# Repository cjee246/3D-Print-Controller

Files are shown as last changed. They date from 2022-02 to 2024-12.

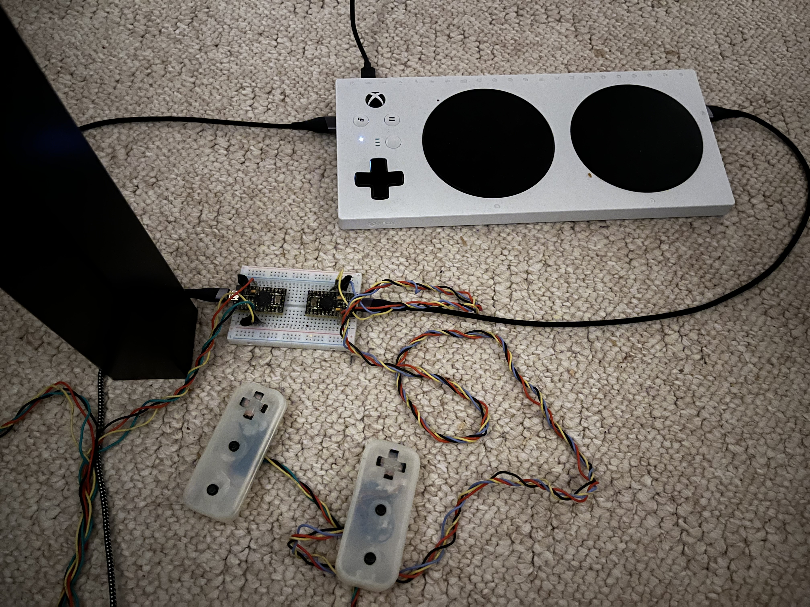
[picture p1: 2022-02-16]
Physical/3D-print control setup.jpg

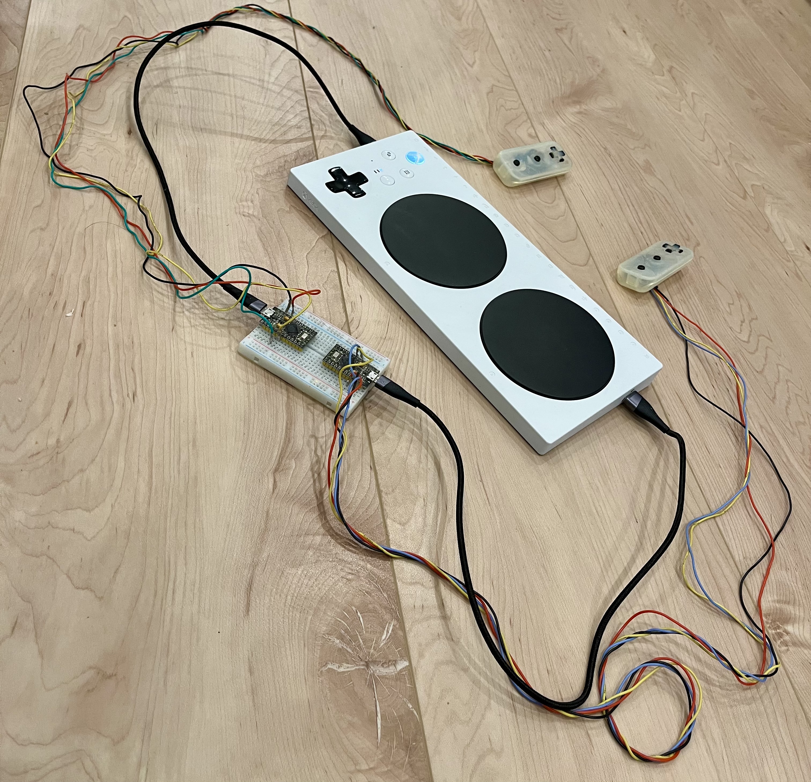
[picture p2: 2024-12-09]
Physical/Controller Assembly.jpg

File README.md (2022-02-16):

# 3D-Print-Controller
Custom made 3D-printed zero-force touch sensitive controller to accommodate chronic pain disability

- see ../0_Single Control for code using configurable controller orientation
- see ../1_Dual Control for code using two controller configuration
- see ../Physical for step files and physical image used in conjunction with xbox adaptive controller

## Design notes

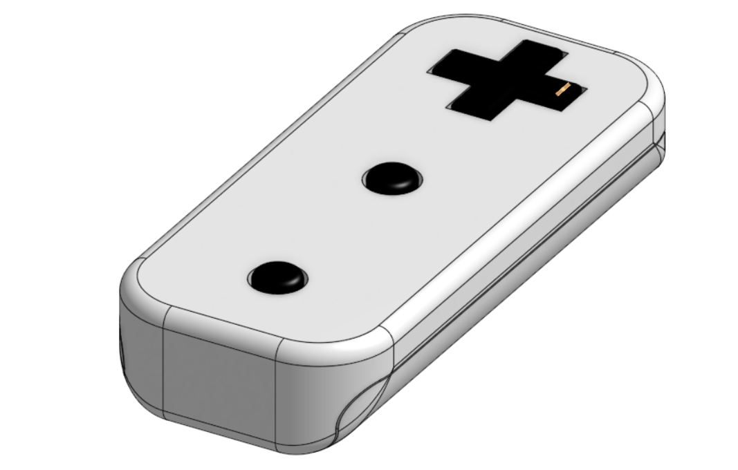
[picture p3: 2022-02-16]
Physical/ctrl.png

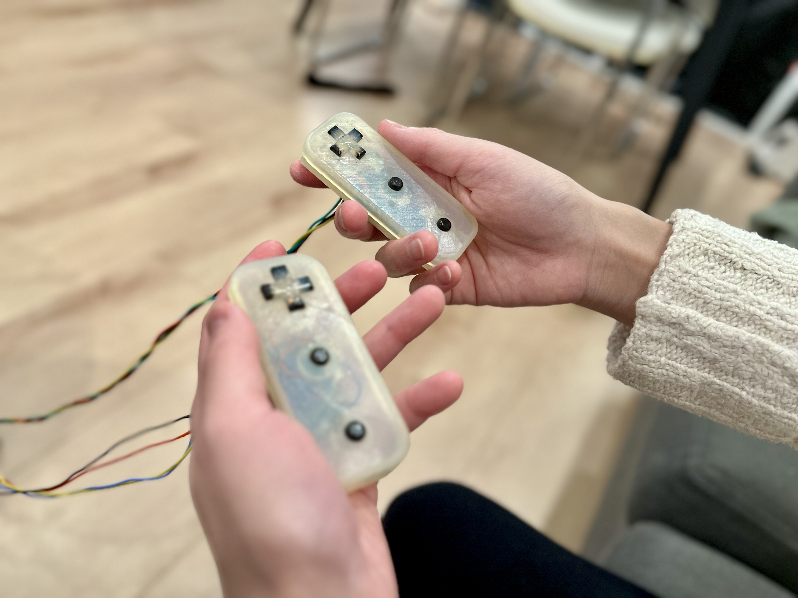
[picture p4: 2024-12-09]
Physical/Controller Held.jpg

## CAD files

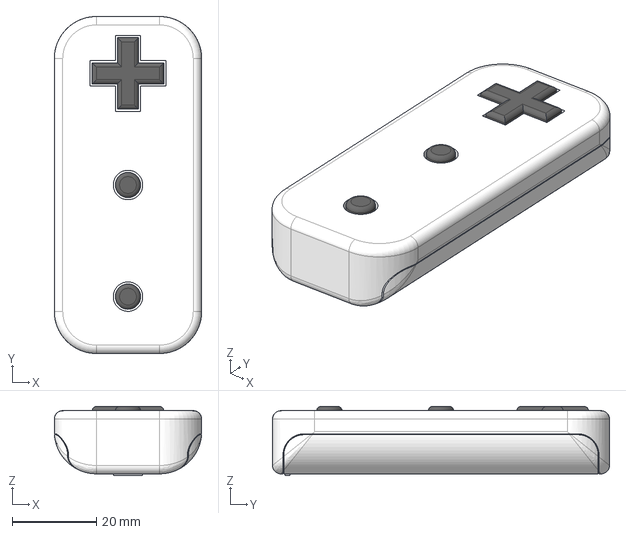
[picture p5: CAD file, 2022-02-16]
Physical/Controller.step
35.0 x 80.0 x 16.4 mm

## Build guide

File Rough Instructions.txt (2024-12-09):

Rough Instructions:
- Sorry for the lack of images, I'm doing this very after the fact

***

Materials:
- 3D printer access
- copper foil tape
- conductive paint
	- I used Bare Conductive Paint
	- This can be excluded if you wish to use copper foil, but it looks sleeker with the paint
- clear spray paint
	- I used Rust-Oleum Painter's Touch 2X Ultra Cover Multi-Purpose Paint And Primer in Semi-Gloss Clear
- wiring
	- I used 28 AWG cut to length and manually crimped coming out of the controller - this means one needs crimps and a crimping tool
		- Alternatively, you can use pre-crimped jumper cables for testing
	- I used 30 AWG wiring for the internals
- soldering equipment
	- Soldering iron, solder, flux, fume extraction, alligator clips, etc.
- Hot glue
	- For fixing the internal wiring in place
- breadboard
- Arduino Pro Micro Atmega32U4 
	- 2 of these if you're doing dual control support
- Capacitive Touch Sensors
	- I used Adafruit 12-Key Capacitive Touch Sensor Breakout - MPR121
- USB-A to micro-USB cable
	- 2 of these if you're doing dual control support

***

Flash code to Arduino Micro Controller
- Micro USB to USB-A into your computer
- If using dual control mode, note that there is a Left and Right Ctrl to flash for each one

Print 3D Model
- 5 pieces
	- 2 buttons
	- 1 d-pad
	- 1 body
	- 1 cover

Attach wiring to pieces
- Buttons
	- Adhere a pad of copper foil to the underside of each button
	- Solder 30 AWG wiring to each button, leave about 4 cm of length
- D-Pad
	- Adhere a pad of copper foil to the underside of each of the 4 sections of the D-pad at the tips
	- Solder 30 AWG wiring to each button, leave about 4 cm of length

Create the contact points
- Using either point or extra foil, extend the conductive area from the bottom of the buttons to the top, where they'll be pressed by user
	- For the D-Pad, I have about 1/2 cm over the edge of each section
- Using paint
	- Takes a bit of trial and error, but mix the paint with water to get a thick consistency that will stick to the surface while drying to a smooth texture
	- Once the paint dries, I recommend going over the buttons and the pad with the clear spray paint
		- this drastically helps prevent the paint from rubbing off from constant contact and having to repaint

Wire the pieces to the sensor board
- Feed the wires through the slots of the body
- Solder them to the correct nodes of the Capacitive Touch Sensor
	- up_ = 0;
	- right_ = 1;
	- down_ = 2;
	- left_ = 3;
	- btn1_ = 4;
	- btn2_ = 5;
- Glue the wiring coming out of the controller slots to prevent the buttons and pad from moving outwards

Finish assembling the internals
- Solder 4 x 28 AWG wires to the sensor board at -- VIN, GND, SCL, SDA
	- Helpful to use different colors
	- I use red (VIN), black (GND), yellow (SCL) and blue/green (SDA)
- Feed the wires through the slot of the cover
- Maneuver the internal cabling to minimize sharp bends and gently close and clip the cover with the sensor board inside
	- New versions of the sensor board may have additional connectors on top, it may not fit if you keep them on...

Connect to the micro controller
- Connect the 4 wires to the Arduino micro controller
	- I like to twist the wires to keep them together
	- I also used a breadboard and crimp connections, but you can also solder or connect directly by other means
- Make sure the pin connections are correct
	- VIN (red) to VCC
	- GND (black) to GND
	- SCL (yellow) to Pin2
	- SDA (blue) to Pin3

Connect micro controller to machine
- If using a computer/pc, it should be recognized as a joystick
	- you can use gamepad testers to check if it is recognized
	- https://hardwaretester.com/gamepad
- If using an Xbox Adaptive Controller
	- plug into one of the USB ports, depending on which joystick you wish to control
	- you will then have to go into the controller app and configure the buttons as you wish (recommend A and B)
	- If all D-pad buttons are pressed at the same time (i.e., with your palm), it registers as another button
		- I use this to trigger the home button

Hopefully all works well at this point -- happy gaming!
